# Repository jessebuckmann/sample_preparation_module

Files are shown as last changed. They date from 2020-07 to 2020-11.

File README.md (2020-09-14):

# Welcome!

You find yourself at the front page of the Utrecht Experiment Design course documentation, edition 2020. 

Welcome! :confetti_ball: :heart_eyes: :smile: :confetti_ball:

## From the course coordinator
 
I am thrilled to be your host in the second edition of the Utrecht Experiment Design (UED) course. My name is Sanli and my goal is to make this course the most memorable one in your program.

Part of the course syllabus is similar to other practical courses you have seen in the past. Other parts might seem a bit unusual at first (e.g. community interactions, story-telling, value exchange), but I hope that by the end of the course, they all make sense to you. Remember, the main goal of this course is to empower you (plural) to be a distinguishable cohort of experimental physics students. Making measurement setups that work and reporting on your experience are means to this goal.

Last year, UED was run for the first time. I had to make a good deal of planning only based on intuition. We had many engaging and constructive discussions and built part of the course structure together. Luckily, students, their mentors and the involved experts at the Physics department, told me they had an overall positive experience, and blessed me with well-intentioned constructive feedback. The course ended with a festive poster presentation. We even had cake and everyone seemed to be very pleased. Some of those students will be your mentors this year. 

## Schedule
From Thursday 3/9/2020 to Monday 2/11/2020
+ Mondays: 11h-18h, Minneart 002 and 004
+ Thursdys: 9:30-12h, MS Teams

+ Thursday, 5/11/2020: __Public Presentation__

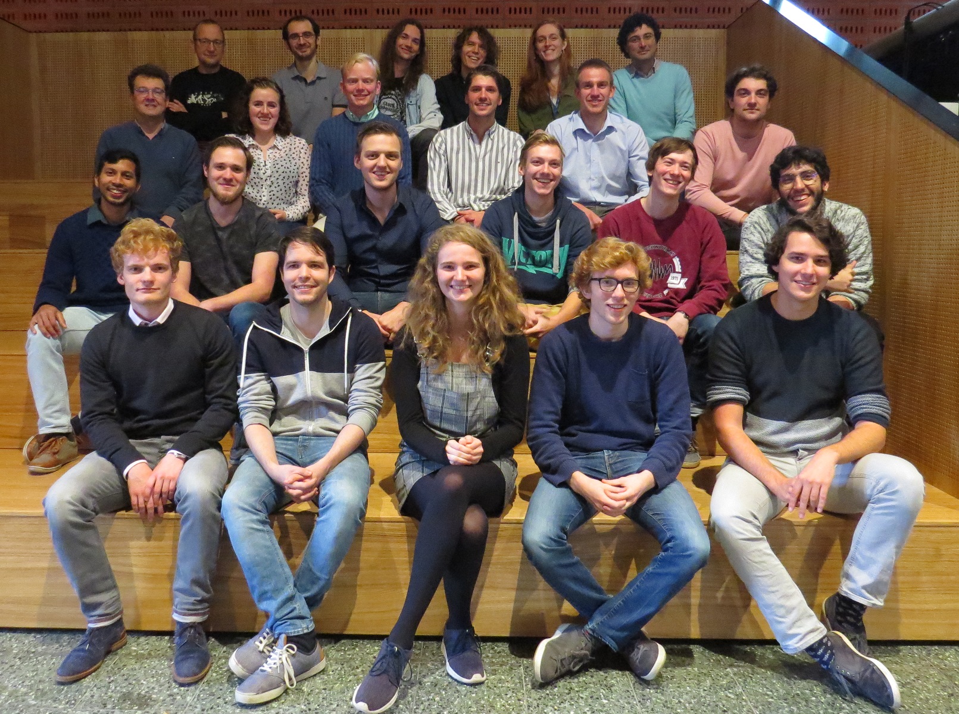
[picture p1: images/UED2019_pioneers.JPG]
cohort 2019

*Group photo with the "πoneers"*

This year, we are equipped with the experience and feedback of your predecessors and have planned a tighter framework. A major part of the course, still, will only be filled in based on your input. 

I hope that this guide can help you navigate through the logistics and instructions of this round. If anything is unclear or if you have questions that are not answered, please reach out to me directly. I am here to help.

#### how to reach me:
+ Email: s.faez@uu.nl 
+ Preferred mode of communciaiton: (direct) messaging on [MS-Team](https://teams.microsoft.com/l/team/19%3a4a388e116e894e4a9ec3a19e32c58294%40thread.tacv2/conversations?groupId=b36d7aae-63c5-44c9-a860-073e4ffd37ae&tenantId=d72758a0-a446-4e0f-a0aa-4bf95a4a10e7)
+ Office: Ornstein laboratory 266 (limited presence due to the Covid19 pandemic)
+ Twitter: [@sanli](https://twitter.com/sanli/)

The files in coordination directory contain most of the information about the course. To start, you can check the [syllabus of the course](Syllabus_2020.md) or check [how to contribute](CONTRIBUTING.md). The files in that directory will be updated during the course (fetch them into your local repo) and the imporant messages will be listed [in updates](UPDATES.md). To make our classes a welcoming and pleasant experience for all participants, please read the [code of concuct](CODE_OF_CONDUCT.md) very carefully, and stick to it.

#### suggestions are very welcome!
Please communicate all your suggestions to the course coordinator (Sanli Faez on MS-Teams) and do not make changes to this document without prior consultation.

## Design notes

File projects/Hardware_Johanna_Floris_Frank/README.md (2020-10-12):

**Welcome To The Hardware Project!** :raised_hands:

We, **Johanna**, **Frank** and **Floris** are the members of the Hardware-Group :v: .
The Hardware-Group aims to connect the techical parts of the box and to provide the experimentalists with a fast and save data transfer. 
Groups performing experiments and environment control give an Arduino-based text output.
The idea is now to connect these 'experiment Arduino's' as slaves to a central master Arduino, using which an I2C communication protocol may be established between them.
The master Arduino may then be read out by the computer running the data analysis and storage software.
The non-triviality lies in the fact that these slave Arduino's also serve as the master device within an experimental set-up by reading out the relevant sensor, which it must to upon request by the central master Arduino.
A more detailed report on context and theory, covering the I2C communication protocol and its main features (also compared to the frequently used SPI protocol), may be found [here](https://git.science.uu.nl/ued2020/experiment-design-2020/-/blob/master/projects/Hardware_Johanna_Floris_Frank/Documentation/Report_on_context_and_theory.md).

**The Experiment(s)**

The first step is getting an I2C communication protocol running between two Arduino's, where a slave sends a simple text message to the master upon the master's request using the [Wire library](https://www.arduino.cc/en/Reference/Wire).
This message may then be printed by the master.

Secondly, a very simple set-up was designed in which a single master Arduino reads out a BME/BMP280 environmental dummy sensor using the [Adafruit sensor library](https://github.com/adafruit/Adafruit_Sensor).

The aformentioned two slaves, i.e. a sensor and a slave sending a text message, were combined into a single-master dual-slave set-up, so that the master receives both measurement values and the text message.

To simulate an experiment Arduino connected to the central master Arduino, a single slave reading out the BME/BMP280 was connected to the master.
It was attempted to have a text tranfser - a data request from the master to the slave, in order to get the measurement startet. Then the slave should read out the data fromthe sensor to send the data as answer to the master.
This set-up did not end up working properly, presumably because the connection of the analog pins somehow leads to the sensor being recognized by the master.

**The Next Steps**

Considering the failure of the previously mentioned set-up, communication between the two Arduino's via the digital port was attempted.
A simple text-based I2C communication protocol between two Arduino's via the digital pins using the [SofwareSerial library](https://www.arduino.cc/en/Reference/SoftwareSerial) was achieved, altough as of yet they are poorly synchronized since the reading and printing my the master is much slower compared to the slave sending the message. (link)
If this is fixed, it should be possible to transfer sensor data between sensor and master upon request of the master. After that, a generalization to a connection with multiple (two for a start) masters may be made.

Should you want to reproduce these circuits, have a look at the [manual](https://git.science.uu.nl/ued2020/experiment-design-2020/-/blob/master/projects/Hardware_Johanna_Floris_Frank/Documentation/reproduction_guide.md).

Let's get this started :fire: !

**Cheerio !** :grin:

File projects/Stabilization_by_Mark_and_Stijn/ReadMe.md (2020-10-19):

In this ReadMe-file, we will place the manual for our folders, as well as our experiments. 

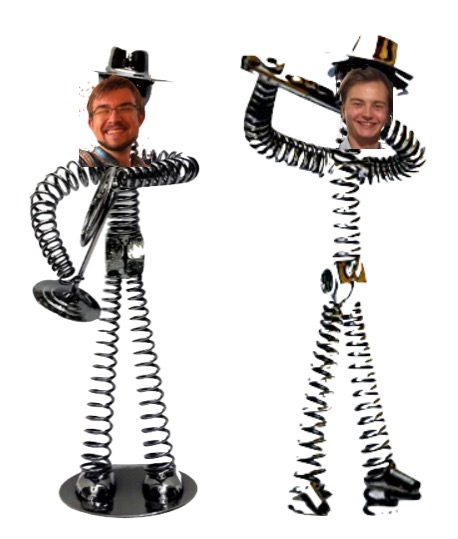
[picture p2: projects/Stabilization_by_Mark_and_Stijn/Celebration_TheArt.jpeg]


The purpose of our experiment was to be able to both see/filter out vibrations, as well as get/keep the experiment level (see our [canvas](project_canvas_-_Stijn_Mark.pptx)).

First off, before you start, we would advice you to get a cup of coffee. You got that? Good, time for the experiments then. 

**Leveling:**
We firstly thought that, in order to get the experiment level, we could use to yaw, pitch and roll (which is something the acceleromotor is able to measure). In the end, you'll find that there is a big problem with trying to do it this way, which is that it resets everytime you restart the acceleromotor. However, it's a good experiment to do, because you will find that this part of the acceleromotor is very precize. 

To do the yaw pitch roll measurments, only the arduino uno, MPU6050 and connectors are needed (in principle). With these components, the MPU6050 can be read out and that's all that’s needed (see ["List_Materials and Code_Used"](Measurements/List_Materials_and_Code_Used.md) for the arduino code that we used, along with our file that explains [how to use the arduino and MPU6050](Measurements/How_to_use_the_Arduino.md)). To do the calibration, a platform that can be rotated is needed. We used a machinist’s division table for this, but other platforms can be used. The machinist table is place in the upright position so (under the assumption that everything is straight) the z-axis of the chip is parallel to the gravitational vector. (again under the assumption we live on a flat earth with homogeneous gravity) When turning on the arduino it self calibrates to gravity so from that point everything is relative to that point. (this implies that for a reproducible result, the sensor needs to be booted in the exact same position)

When the sensor is setup and measuring the table can be rotated around the clock. This is done on increments of 1 degree from 0 < theta  < 10, than 5 degree intervals up to 90 degrees and from this point on only every 10 degrees to complete the circle. Whilst setting the angles it has to be taken in account that there is some mechanical give in the system. This could introduce a new error in the system when not dealt with correctly. To compensate for this give, the knob has to be put onder strain on the same side of each measurement point. This means either at the beginning or end of the give.  On each of the set angle points the yaw pitch and roll have to be manually read out. When all data is collected the points can be plotted in a program of your own choosing.

The Full Setup that we used can be found in the ["SetUp1"-folder](Measurements/Yaw_Pitch_and_Role_Measurements/SetUp).

The rest of the data and graphs that we gained, can be found in the ["YawPitchRole"-folder](Measurements/Yaw_Pitch_and_Role_Measurements).

**Vibrations:**
The main experiment that the "experiment-group" wanted to do, was the Cavendish-Experiment. This means that frequenties below 10 Hz will be "deadly" to the experiment. Our main objective thus became a little more specific than what we started with. However, we weren't able to find a good way to "create" these low frequenties (since low frequenties posses low energy), thus we also weren't able to measure them and thus see if our system could filter them out. Because of this, we have only taken a look at frequenties between 20 and 100 Hz, because those we could create and see. 

In a vibration experiment, one needs 3 things:
- Something that creates the vibrations
- A mass that vibrates, on which you can stick your measuring device
- A device on which you can see the data measured.

In our case, that something that creates vibrations became a bass-speaker. However, if one can't get a viable machine that gives off a constant frequency, you can also use one single strong wave(for example made by the hit of a hamer on the work-surface). Our bass-speaker had been secured to a woaden board, which we put on some form of dampening substance. The main reason that we started to use such a dampening substance, was because otherwise, the board would vibrate off the table. However, by doing this, we "accidentally" created a double-spring system, which is better at filtering out frequencies. 
On the other end of the board, we can then put our mass with our measuring device (the acceleromotor). Between the board and the mass, we can then prepare our system (this can be springs, a dampening substance, or in the easiest case: nothing). To see what has been measured, one has to take a look at what kind of acceleromotor one has. For our experiment, we used an acceleromotor that could directly be plugged into an oscilloscope, meaning that we could visualize the waves on there. In some cases, one can also plug the oscilloscope into the computer, and thus you can easily extract the data. In our case, we could only get possesion of a older type of oscilloscope, which wasn't able to do this (unless we would have found a floppy-disc and a way to get this floppy-disc into our computer).
However, one can also use the computer and the waveforms-programme of digilent, which is also able to visualize waves. The only thing that's left now, is to show how the system that you have taken a look at reacts to a certain frequency. This is done by making a bode plot, which can be done by a very good oscilloscope, but you can also do it by hand (which takes a lot longer).

If neither of these 2 is possible, one doesn't have to build our entire setup, in order to still be able to see that the accelerometer can measure waves. One can also "visualize" the waves by just directly looking at the acceleration-output that you get when running the arduino-file "MPU6050_DMP6" (see our arduino-explanation file how to find this). To do this, all you need is the arduino, the accelerometer and a work-surface. When looking at the raw data, you should see that the acceleration changes when you hit this work surface. 

The Full Setup that we used can be found in the ["SetUp2"-folder](Measurements/Acceleration_Measurements/SetUp). We als made a ["Materials and Code_Used"-file](Measurements/List_Materials_and_Code_Used.md) where you can find all the materials and code that we used for our setup.

The rest of the data and graphs that we gained, can be found in the ["RawSignals"-folder](Measurements/Acceleration_Measurements/RawSignals) and the ["FFT"-folder](Measurements/Acceleration_Measurements/FFT). As said before, we only have pictures of our data, since we weren't able to get an oscilloscope from which we could actually extract our full data. Because of this, there is also this added error-bar in our graphs. 

If you want to see more about what we did with our setup, see our [First Rapport](Rapport_after_first_weeks.md).

**Hazards:**
- If the people after us decide to also use a machinist’s division table (on the mill), keep in mind that you are working with heavy machinery. So first off, don't consume any alcohol while operating this machines, but also make sure the machine is turned off when you are changing the settings manually.
- Don't shake/drop the acceleromotor to much (nor the arduino), since this is fine equipment. 
- If you use a bass-shaker, keep in mind that it can vibrate off the worksurface, as well as overheat. 

**Needed Contact Information:**

Stijn Helsloot, s.helsloot@students.uu.nl

Mark Waterlaat, m.m.a.waterlaat@uu.nl

Dante Killian, d.killian@uu.nl (Contact person for equipment)

Rene Barthel, (Contact person for equipment)

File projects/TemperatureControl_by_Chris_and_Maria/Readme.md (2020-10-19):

Hello everyone!

We (Chris and Maria) are the team that deals with the temperature control of the box for the actual experiemnt!

Scope of the project:

We aim to measure the temperature and send the value each minute to the software team. Except from that, with the use of peltier we will cool or heat the box when is necessary. More about that you can find in the template_Article inside the file [documantation/data](https://git.science.uu.nl/ued2020/experiment-design-2020/-/tree/master/projects/TemperatureControl_by_Chris_and_Maria/documantation/data), where is also the schematic of the circuit and the code we use (so far).

About the instructions:

The instructions on how to reproduce the setup can be found in the file [Instructions](https://git.science.uu.nl/ued2020/experiment-design-2020/-/tree/master/projects/TemperatureControl_by_Chris_and_Maria/Instructions) together with some photos that will help you! We will soon add in that file the updated instructions based on our feedback. **Notice**: We are planning to make some more changes on our setup and we have not taken so far accurate measuraments so do not expect to take something. We will inform you through README about the changes we will have! The aim for now is just ro reproduce the setup. 

In the file [feedback](https://git.science.uu.nl/ued2020/experiment-design-2020/-/tree/master/projects/TemperatureControl_by_Chris_and_Maria/feedback) except from the peer feedback and by the Coordinators you will also find our response!

Here also you can find our canvas as well as our project and personal goals!

If you need further information on something and you believe that it should be here please contact us and we will fix it as soon as possible! :)

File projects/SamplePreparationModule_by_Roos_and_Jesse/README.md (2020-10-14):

### Sample preperation module
By Jesse and Roos

### Project description
In this project a Sample preparation module is build. It has some of the features typically found in a fumehood, but with an all new design. The sample preparation module enables the user to prepare samples without contaminations in a well ventilated area. The box will be modular, meaning that the user can perform multiple kinds of experiments within the box. The user can supply the tools that are needed for the specific experiment currently equiped in the off-grid lab. 

Typically a fumehood is a very expensive lab component. Looking at the [cost](https://git.science.uu.nl/ued2020/experiment-design-2020/-/blob/master/projects/SamplePreparationModule_by_Roos_and_Jesse/project_details/cost_breakdown.md), designing your own fumehood might have several advantages. Obviously you need to live up to some of the general features a fumehood must have e.g. ventilation and chemically resistant worksurface. Besides being much cheaper, you can design the fumehood in a way to simplify the sample preparation you need to do.

For the general construction of the fumehood the [building progress](https://git.science.uu.nl/ued2020/experiment-design-2020/-/blob/master/projects/SamplePreparationModule_by_Roos_and_Jesse/project_details/building_progress.md) is available, along with several [photos](https://git.science.uu.nl/ued2020/experiment-design-2020/-/tree/master/projects/SamplePreparationModule_by_Roos_and_Jesse/Photos) of the various stages of construction. While this construction might not live up to the features of a real fumehood, it does offer a degree of protection and a good working environment for the prepartion of some typical samples that are used in experiments.

For reproduction of builing the box you can read the [building progress](https://git.science.uu.nl/ued2020/experiment-design-2020/-/blob/master/projects/SamplePreparationModule_by_Roos_and_Jesse/project_details/building_progress.md). Testing of the box can be found in the [testing directory](https://git.science.uu.nl/ued2020/experiment-design-2020/-/tree/master/projects/SamplePreparationModule_by_Roos_and_Jesse/Testing). This directory contains two different testing procedures. One for the [airflow/ventilation](https://git.science.uu.nl/ued2020/experiment-design-2020/-/blob/master/projects/SamplePreparationModule_by_Roos_and_Jesse/Testing/testing_airflow.md) and one for the [chemical resistance](https://git.science.uu.nl/ued2020/experiment-design-2020/-/blob/master/projects/SamplePreparationModule_by_Roos_and_Jesse/Testing/testing_coating.md). For the reproduction of these testing results the instructions can be found in the [instructions](https://git.science.uu.nl/ued2020/experiment-design-2020/-/tree/master/projects/SamplePreparationModule_by_Roos_and_Jesse/peer_instructions) Here you will find an additional README to help you get started.

Main features:
- [ventilated](https://git.science.uu.nl/ued2020/experiment-design-2020/-/blob/master/projects/SamplePreparationModule_by_Roos_and_Jesse/Testing/testing_airflow.md), to carry away fumes
- [spill proof](https://git.science.uu.nl/ued2020/experiment-design-2020/-/blob/master/projects/SamplePreparationModule_by_Roos_and_Jesse/Testing/testing_coating.md), the workspace has high chemical resistance.
- [air tight](https://git.science.uu.nl/ued2020/experiment-design-2020/-/blob/master/projects/SamplePreparationModule_by_Roos_and_Jesse/Testing/testing_airflow.md), ensure that the fumes will only go out through the pipe.

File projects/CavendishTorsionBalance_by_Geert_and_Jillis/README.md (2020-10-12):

# Cavendish Torsion Balance

Welcome to the folder which contains all the information on the Cavendish Torsion Balance project.  

The project is run by Jillis Schokking (j.b.e.schokking@students.uu.nl) and Geert Schulpen (g.h.a.schulpen@students.uu.nl).
You can reach us by [MS teams](https://teams.microsoft.com/l/channel/19%3a17671f7d35194c9aa6a368c449fd96fe%40thread.tacv2/grand%2520project?groupId=b36d7aae-63c5-44c9-a860-073e4ffd37ae&tenantId=d72758a0-a446-4e0f-a0aa-4bf95a4a10e7) or in person if we by chance are around. 

## Description of the project
We try to measure the gravitational constant G by way of a torsion balance, which was first done by [Henry Cavendish](https://www.jstor.org/stable/106988). The current setup is a redesign of the basic setup as used by first year students. This was necessary due to the size constraints of the modular experiment box. The experiment setup is almost finished, and can be used in its current state to measure the gravitational constant. A short overview of the context and theory for the experiment can be found [here](ContextAndTheory.md). An instruction manual for working with the setup can be found [here](instructionManual.md). Proper measurements will require carefull calibration. 

## Current state of the project (roadmap)
At present, our setup should be able to measure the gravitational constant. Electronic elements are plug and play. Only the installation of WaveForms is required. In its current state we have completed the following items:
- Found a temporary bed with enough vibrational damping.
- Moddeled and 3d printed all necessary structural parts
- Implemented a way to measure angles (Digital Discovery 2, Laser, Sensor and Modulator)
- Automatic rotation of the outer ring (Arduino, belts, servo's)
- Construction of the halter.

The following items still need to be finalized:
- Construction of a proper bed that fits in the modular experiment box.
- An automatic release mechanism for the torsion balance.

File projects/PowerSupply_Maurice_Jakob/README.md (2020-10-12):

# List of files you may be looking for (if not, ignore this section)
- [Report context and theory](./documentation/report_context_theory.md)
- [Project goals](./documentation/project_foals.md)
- [Instructions](./documentation/Instructions.md)
- [Personal goals Maurice](./documentation/Personal_Goals_Maurice.md)
- [Personal goals Jakob](./documentation/personal_goals_jakob.md)

# Power supply for Experiment box

In this subproject considerations and the design of a power supply that suffices for the needs required are made.
The goals of this project are briefly presented in the [canvas](./documentation/project_canvas_ps.pptx) and further elaborated in this [report](./documentation/report_context_theory.md).

To settle on the right approach a comparison between different levels of DIY was made which can be found [here](./documentation/Comparison_powerbank_DIY.md).
The major difference is the level of knowledge regarding electronics required to build it.

A current list of parts for this project can be found [here](./documentation/list_of_components.md).
The current plan consist of a powerbank (5V), 12V lead acid and inverter to provide all the needs specified.
A load-switch and monitoring system will provide the safety and communication with other parts of the box.
It is further expanded with a solar panel to charge the station remotely.

How to put everything together is documented in the [instructions](./documentation/Instructions.md). 
There is also a separate [documentation](./documentation/Arduino/Arduino_Instructions.md) about monitoring the battery voltage with the use of an arduino.

### Our first milestone
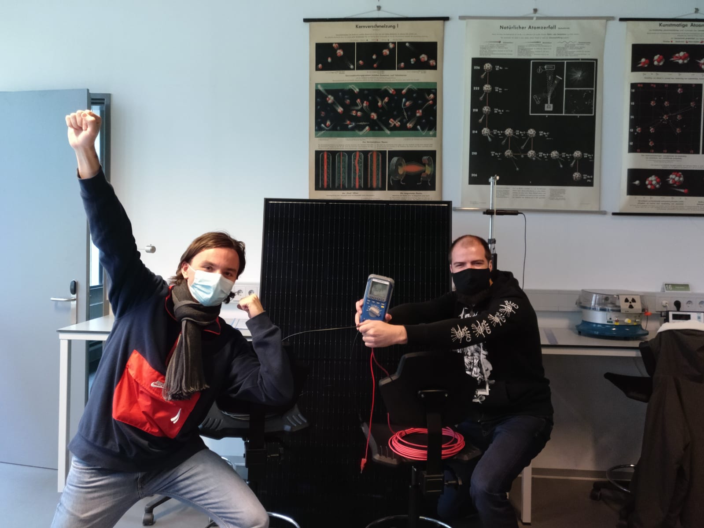
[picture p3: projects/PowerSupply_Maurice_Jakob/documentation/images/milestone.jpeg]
milestone


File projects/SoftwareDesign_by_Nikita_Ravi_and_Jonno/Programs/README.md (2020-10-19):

Hi honorable User!

If you haven't already, please first follow the [installation guide](projects/SoftwareDesign_by_Nikita_Ravi_and_Jonno/Installation_guide.md). 

There are four options to use the program.
1. Measure using a real Arduino and Analog Discovery 2
2. Measure using a real Arduino and a simulated Analog Discovery 2
3. Only use a real Analog Discovery 2
4. Only use a simulated Analog Discovery 2

See below on how to set up each one of the four options.

Once you get the BIMBO up and running, you can navigate through the tabs and press the start/stop buttons to start measuring. When pressing scan on the Analog Discovery 2 tab, a window pops out which allows you to scan the data and save it over time. If you browse to save the file, it will save as a .nc. However, you can still change the extension before you save it to for example csv. You can also edit the file path by just typing in the textbar instead opening the browse window. Whatever extension is there, if you open it with notepad it will still be in the csv format. The is an example output file [here](projects/SoftwareDesign_by_Nikita_Ravi_and_Jonno/Programs/Example_Measurements/exampleMeasurementAD2.csv). If you have ticked the Store config box it will also save a file with your config that looks like [this](projects/SoftwareDesign_by_Nikita_Ravi_and_Jonno/Programs/Example_Measurements/exampleMeasurementAD2.yml).  

For scanning any data coming in via an arduino, e.g. temperature or pressure, press 'start scan' in the designated tab. This will start an invisible scan in the background. Pressing 'stop scan' will terminate the scanning procedure and create a .txt file in the source folder with the acquired data in the format: 

\[TemperatureArray]   
\[TimeArray]

For examples see [here](projects/SoftwareDesign_by_Nikita_Ravi_and_Jonno/Programs/Example_Measurements/exampleMeasurementTemp.txt) and [here](projects/SoftwareDesign_by_Nikita_Ravi_and_Jonno/Programs/Example_Measurements/exampleMeasurementPres.txt).

If you would like to use an Arduino. Please make sure it outputs the data in the format: time(in ms),temperature(as float),pressure(as float). If you have no way of getting actual data from an arduino, or don't know how, you can simply make it output simulated data in the correct format by uploading [simulation_for_arduino.ino](projects/SoftwareDesign_by_Nikita_Ravi_and_Jonno/Programs/simulation_for_arduino.ino) to your arduino by using the [arduino IDE](https://www.arduino.cc/download_handler.php?f=/arduino-1.8.13-windows.exe)! In case you are using an Arduino Due, be sure to use the programming port on the arduino to upload any programs, it's the micro-usb port closest to the power input.

A list of known bugs can be found [here](/projects/SoftwareDesign_by_Nikita_Ravi_and_Jonno/Programs/Bugs.md).

In preparation of any of the four following options, open your preferred Python IDE and open the five .py files in experiment-design-2020-master\projects\SoftwareDesign_by_Nikita_Ravi_and_Jonno\Programs

**1. Arduino + real Analog Discovery 2**
- [ ] In the BIMBO_Interface.py uncomment the ArduinoWidget import in line 1.
- [ ] Uncomment the import from line 16 where the real controller is imported.
- [ ] Comment the import from line 17 where the simulated controller is imported.
- [ ] Uncomment lines 71 and 72 where the tabs for the Arduino are added .
- [ ] In order to start using the program, it is essential you plug in the Arduino measurement unit and make sure that it is outputting data in the required format.
- [ ] Once you have done this you have to check which COM-port is used to communicate with the device. This can be done in Windows by opening *Device Manager* and finding **Ports**. There it will say what COM-port is used. For Mac type ls /dev/* in the terminal to find the com port in the form /dev/tty.usbmodem* where * is the number. 
- [ ] FOR WINDOWS: Now go to the ArduinoWidget.py file and change the 'COMX' in line 17 to whatever COM is used by your device.
- [ ] FOR Mac: Change line 17 to: arduinoData = serial.Serial(port='/dev/tty.usbmodem14201', baudrate=9600)
.
arduinoData = serial.Serial(port='/dev/tty.usbmodem14201', baudrate=9600)

You are all set to go, just run the BIMBO_Interface.py with a Python interpreter in for example Spyder!

**2. Arduino + simulated Analog Discovery 2**
- [ ] In the BIMBO_Interface.py add the ArduinoWidget import to line 1 if it is not there.
- [ ] Comment the import from line 16 where the real controller is imported.
- [ ] Uncomment the import from line 17 where the simulated controller is imported.
- [ ] Uncomment lines 71 and 72 where the tabs for the Arduino are added.
- [ ] In order to start using the program, it is essential you plug in the Arduino measurement unit.
- [ ] Once you have done this you have to check which COM-port is used to communicate with the device. This can be done in Windows by opening *Device Manager* and finding **Ports**. There it will say what COM-port is used. For Mac type ls /dev/* in the terminal to find the com port in the form /dev/tty.usbmodem* where * is the number. 
- [ ] FOR WINDOWS: Now go to the ArduinoWidget.py file and change the 'COMX' in line 17 to whatever COM is used by your device.
- [ ] FOR Mac: Change line 17 to: arduinoData = serial.Serial(port='/dev/tty.usbmodem14201', baudrate=9600)

You are all set to go, just run the BIMBO_Interface.py with a Python interpreter in for example Spyder!

**3. Only real Analog Discovery 2**
- [ ] In the BIMBO_Interface.py remove the ArduinoWidget import from line 1.
- [ ] Uncomment the import from line 16 where the real controller is imported.
- [ ] Comment the import from line 17 where the simulated controller is imported.
- [ ] Comment lines 71 and 72 where the tabs for the Arduino are added.

You are all set to go, just run the BIMBO_Interface.py with a Python interpreter in for example Spyder!

**4. Only simulated Analog Discovery 2**
- [ ] In the BIMBO_Interface.py remove the ArduinoWidget import from line 1.
- [ ] Comment the import from line 16 where the real controller is imported.
- [ ] Uncomment the import from line 17 where the simulated controller is imported.
- [ ] Comment lines 71 and 72 where the tabs for the Arduino are added.

You are all set to go, just run the BIMBO_Interface.py with a Python interpreter in for example Spyder!

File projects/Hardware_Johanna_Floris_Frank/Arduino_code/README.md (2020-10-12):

**digital_master and digital_slave**

Simple scripts for I2C communication between a master and slave Arduino via the digital pins.

**master_reader and slave_reader**

Simple scripts for I2C communication between a master and slave Arduino via the analog pins.

**BME**

BME.ino can be uploaded to a master Arduino connected to a single (BME) sensor and possibly a slave Arduino. The master Arduino then reads the sensor output and, if present, the text-based message the slave sends directly. Should you want to use the second Arduino, the slave_reader.ino sketch should be uploaded to the slave device.

**Hybrid_Master and Hybrid_Slave**

The hybrid experiment has a network of multiple Arduinos being able to send data to a master Arduino. Hybrid_Master.ino can be uploaded to an Arduino, which then acts as the master Arduino requesting data from subscriber (slave) Arduinos and shows this data. Hybrid_Slave.ino can be uploaded to Arduinos connected to (BME) sensors. These subscribers then read the sensors and give the data to the master upon request.

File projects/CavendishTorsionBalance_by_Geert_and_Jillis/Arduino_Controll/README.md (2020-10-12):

The other file in this directory has the code to control the arduino and continuous servo for the Cavendish Balance.  
To control the arduino open this in the [arduino web editor](https://create.arduino.cc/editor) (or in your own local installation of the arduino editor). 
Set the board/port dropdown to "Arduino Due" and open the Serial Monitor from the sidebar.
You can send the code to the arduino by clicking on the arrow next to the board/port dropdown, the arduino will send a "hello world" message when the initiallization has worked.
More information on the arduino web editor can be found [here](https://create.arduino.cc/projecthub/Arduino_Genuino/getting-started-with-arduino-web-editor-on-various-platforms-4b3e4a)

The controller assumes the balls are in a neutral position at the start, they are midway between both measurement positions.
The turningtable is controlled by sending single characters to the arduino; E, L, R, S, l and r.
- S will turn the turningtable from the neutral position to one of the measurement positions
- E will turn the turningtable from one of the measurement positions to the neutral position
- L or R will turn the turningtable from one to the other measurement position
- l or r will turn the turningtable slightly in the same direction as L and R respectively

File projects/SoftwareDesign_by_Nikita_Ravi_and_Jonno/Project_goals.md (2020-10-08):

*Utrecht Experiment Design 2020*

# Project goals

### POP

+ **Purpose**: to define your targets for the project you have chosen and to keep your eyes on the ball 
+ **Outcome(s)**: list of checks and measure for evaluation of your project
+ **Process**: self-reflection and discussion with your mentors

PROJECT NAME: Software Design
PROJECT MEMBERS: Mikita, Jonna, Ravi

## Project goals (fill this at the start of the course)
* We want to make an intuitive program that can be used by people without any experience
* We want to be able to visualise data in said program
* we want to be able to adjust sensors in said program if needed
### Subgoals
* Make the model part
* Make the controller part
* Make the view part
* Transfer the sensor-signal to data
* Make an artificial data stream to test the model and interface

## Mid-course review of goals (fill this mid-course)

* We want to make an intuitive program that can be used by people without any experience
* We want to be able to visualise data in said program
* We want to be able to adjust sensors in said program if needed

Subgoals

* Create an arduino controller
* Adjust the AD2 controller (save files into text, voltage vs time)
* Make the general interface with tabs
* Make an artificial data stream to test the model and interface (CHECK!)

## Final review of goals (fill at the end of the course)

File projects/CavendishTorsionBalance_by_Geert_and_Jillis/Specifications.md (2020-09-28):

# Power

| | |
| ------ | ------ |
| Operating Voltage | 230 V (modulator), 5V (servo's) |
| Power Usage | We have to check (probably fairly low; small laser (1mW output) and a light sensor) |
| input type | AC |

The input voltage goes into a modulator to make the setup filter outside light. It directly controls the LASER and sensor. These use a much lower voltage. As such the modulator includes a transformer to transform back down to ±5V and ±8V. We feel it should be possible to cut out this transformer and directly feed the modulator, but the lab technician says otherwise for now. The 8V channel would need to be balanced.

# Size
| direction | size (cm) |
| ------ | ------ |
| width | 30 |
| depth | 50 |
| heigth | 35 |

# Vibration control
The experiment is vulnerable to low frequency vibrations. The natural frequency of the balance is 1 Hz. Therefore a low pass frequency dampening system with a threshold of 0.1 Hz would be desirable. 0.1-10 Hz couples strongly to our pendulum.

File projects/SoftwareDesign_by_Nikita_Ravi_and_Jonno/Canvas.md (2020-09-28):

# Problem
1. The raw data from the sensors is not processe
2. The processed data is not displayed
3. There is no way to control the sensors

# Solution
Make an intuitive UI that shows the current sensor values and can send data to sensor. 
It should also be able to save the data for analysis.

# Key metrics
* The data is correctly displayed and devices can be controlled. 
* This can be tested with artificial data stream.
* You should be able to use the interface with very minimal training. 
No programming knowledge needed, only a small one page explanation about the program.

# Resources required
* A display and raspberry pi (could also be combined as an external laptop)
* Data from the sensors
* Python knowledge about GUIs and controller
* Know which protocols are used
* Packages for those protocols and labphew package
* Power supply for raspberry pi or to (slowly charge laptop)

# Contributor Profiles
The contributors will be people on the internet that made open source packages.
Ideally, a contributor has extensive programming knowledge and has worked with interfacing before.
The other contributors will be the people that provided the data and hardware.

# User Profiles
Our early adopters will be the people that build the sensors. 
They will rely on our interface to do measurements.
The final users will be the people that make use of the measurement station.
They will need it to controll the device and make actual use of it.

# Contributor Channels
Once people want to introduce new sensors, our program should be good enough to build upon.
This way they will not have write their whole thing from scratch but can use/edit/incorporate our program.

# User Channels
They have basically no other options apart from writing a program themselves.
What we should do is make a program that is good enough that they will not want to write their own.

# Unique Value Proposition
We will make sure that even people that do not have programming experience or knowledge can still use our device.
Our project will also greatly simplify the use of the box.
It is also needed to connect the different parts of the box to be able to do a cohesive measurement.

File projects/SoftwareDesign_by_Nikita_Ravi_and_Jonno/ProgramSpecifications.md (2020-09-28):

| **Component**                | **Specs**                                                    | **Done by** |
| ---------------------------- | ------------------------------------------------------------ | ------ |
| General interface            | * Dropdown button/tabs to swap between controllers<br />* Exit button<br />* Window to display graphs<br />* Overview mode of all graphs<br />* Ability to save data |Ravi        |
| Digilent AD2 Controller      | * Live feed of the inputs (from AD2 to computer) <br />* Ability to control outputs (from computer to AD2)<br />* Ability to save the inputs over time |Mikita       |
| Arduino text base controller | * Ability to display live feed of text-based inputs (from Arduino to computer)<br />*Ability to save inputs over time |Jonno        |

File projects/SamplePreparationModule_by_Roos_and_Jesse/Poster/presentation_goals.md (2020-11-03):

# Experiment Design 2020

## Symposium self-reflection

project, team: Sample preparation module, Roos de Boer and Jesse Buckmann

The purpose of this self-reflection is to learn from the exercise of presenting your project to a public audience. Answer the preparation questions **before** the online symposium and evaluate them based on your experience **after** the end of the symposium

## Preparation

### Content: 
+	What makes your pitch attractive? 

- Suggestions of possible problems/negatives and explaining how they are not present.

+	What do you want the visitors to learn from your pitch? 

- What the purpose of the sample preparation module is. 

+	What elements have you deliberately put in your presentation to reach your goal?

- Comparison of the sample preparation module to an actual fume hood so you can see the advantages of the sample preparation module.
- Mentioning problems and stating that the sample preparation module is the solution.

### Performance:
+	What is **your** goal of presenting your pitch?

- For people to become interested in the sample preparation module and for them to think of it as a good alternative for the fumehoods.

+	What do you want the visitors to remember after coming to your discussion room?

- That the sample preparation module is cheap, easy to build and widely applicable.
- That you can still do experiments in times of Corona.

+	Which indicators show to you that your visitors are engaged with your message?

- They understand the advantages of the sample preparation module and might consider how it could be applicable in certain situations.

## Evaluation
+ 1.	What worked well about your pitch and presentation?
+ 2.	What did not work as you expected?
+ 3.	Considering your own indicators, how do you evaluate the success of your final presentation?
+ 4.	What feedback have you received from the visitors about the project and about your way of presenting it?

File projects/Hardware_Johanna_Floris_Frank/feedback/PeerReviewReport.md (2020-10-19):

# Reproducibility report

## Experiment/team: 
Hardware by Floris, Frank and Johanna

## Reviewers: 
Geert, Maria and Olaf

## Report 

### Documentation:

1.	Could you understand the purpose of the experiment? Explain.
The purpose of the experiment is to rebuild three set-ups connecting different arduinos and sensors. Within the larger project this is of importance since we want all the different components to be connected to each-other and to have communication between them. 

2.	Were the safety instructions clear?
Yes, since there were no safety instructions they were clear.

3.	How helpful is the documentation for reproducing the measurement?
The documentation was not quite complete. It is assumed that you have prior knowledge of arduino's and of the hardware. It would have been helpfull if the instructions would have included more detail on the placement of the wires (e.g. to which pins in the arduino the sensor had to be connected) in the arduino and or the sensors. It would have helpful as well if there would have been more instructions on what every element does and how it looks like (e.g. we did not know what the sensors look like and could not find them in the beginning).

4.	Did you get stuck at some point? What extra help did you need to proceed?
Yes, from the instructions alone it was not clear if we needed to use one arduino, or use them both at the same time. Luckily this was mentioned briefly in the readme so with that information we were able to figure out the set-up. Also, Maria and Geert had prior knowledge of working with arduinos and breadboard so we did not have to look up how they work in more detail to reproduce the set-ups

5.	Are you guided to reproduce previous measurements? How easily could you navigate through the project documentation?
The links to the necesarry sketches were placed in the instructions so this was quite convenient. We did miss clear goals by which we could check if our set-ups lead to the same results as the project group. We had no way of checking this. It was possible to deduce this for the first two set-ups from the code but not for the third set-up.

6.	What can be improved in the documentation?
The instructions could be improved by adding schematic drawings of each set-up. This would make the placing of all the components and wires clearer and easier to reproduce. Also provide a clear goal to the experiment, what should each set-up do exactly? How can we confirm if it is working properly?

### Measurements:

1.	Can you operate the setup with the provided instructions?
We answered this question in the previous part.

2.	How close were the results you obtain to the previously reported results?
We do not know precisely since we do not know the exact results the project group obtained. We did find however that the arduino's and sensors were communicating with the master arduino.

3.	Can you understand and explain the analysis procedure to a third person?
Not really since there is no analysis procedure. I think I have a general sense of how the code works but I could not explain it in detail.

4.	Is the setup robust and safe to operate? 
Yes it was safe

5.	Did you encounter any issues? Could you troubleshoot those without contacting the owners?
Yes, we did not know how the sensor looks like. We were able to troubleshoot this by googling for the name of the part we did not recognize.
We also had problems with how to connect the sensor to the arduino, but that was solved by trying a couple of variations.

6.	What part of the measurement procedure did you appreciate most?
It is nice that the Arduinos can communicate.

### Interactions:

1.	Could you relate to the stated goal of the project?
Yes, we also want to be able to control the different elements in the box from one central place.

2.	Which instructions did you need from the owners on top of the written files?
We could had asked them the results they had in order to know if ours were correct.

3.	Does the experiment accomplish its stated purpose?
It is not accomplished because the data from the sensor could not reach the second arduino. However, the owners of the project are already aware of this.

4.	What do you recommend to the project owners to improve their complete package?  
It seems that the problem in the Hybrid codes comes from the fact that a float-type has to be cast to a byte-type and this is not done explicitly.
It might be that [this](https://forum.arduino.cc/index.php?topic=577373.0) web-page can help with this.
The master arduino does send output when wiring incorrectly (SCL-A4 slave-A4 master, SDA-A5 slave-A5 master), maybe this helps in solving the problem, it did not send output when wiring correctly, as indicated by one of the owners of the project.
It would be nice to create a wiring diagram/pictures of the final setup.
It would be nice to include some documentation for people who did not yet work with an Arduino yet.

## Respone from project group: 
Thank you for the documentation.
It was indeed a bit vague how to connect the wires based purely on text. Wiring diagrams for the different set-ups are now included, as an overview diagram of an Arduino UNO board and the sensor. 
Hopefully this also solves probles regarding the recognision of the sensor component.
 
In our experience, the desired output was somewhat clear from the description of the set-up itself. 
However, since your experiences were different, a have added this more explicitly to the reproduction guide.
In addition, a mre detailed description on what the COM port output should read if the set-up is repeated.

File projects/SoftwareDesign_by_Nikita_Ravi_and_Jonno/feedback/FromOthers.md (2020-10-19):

## notes

complicated with the installation files, could be prepackaged in a zip  
**This could indeed be done, be would need to be redone everytime a file changes. So for now we will leave it like this.**  

labphew installation caused many issues, but we managed to get it working on one machine.  
**Nice you at least got it working on one machine.**  

Then a second readme about the usage start with "once you get the BIMBO up and running", it feels like some intermediate steps are missing that connect the two files.  
**Added meaning of BIMBO to the first README.**  

Could use some additional steps for the installation of the arduino or make it clear if its necesary or not, given the pre-installed arduino  
**We do not really know how to make it cleared, as there is already an explanation of how to upload a simulation program to an Arduino. We could have more clearer stated that the Arduino's given to you were already preinstalled. Also, the issue of data output is more something for the sensor people.**  

Steps for finding COM port are seperated, even though they are a single step. was slightly confusing.  
**Yes good point. Edited this in the README to make it one step.**  

unclear where the savefile goes for AD2, it says a path, which does not exist on the user's PC. Browse button does not work, gives error in spyder 'model labphew has no attribute 'parent_path''.  
when trying to save to a new path by writing it, it gets permission denied or no such file or directory.
**We were not able to reproduce this bug. For us the browse button works. There is also a default path already written, which you can edit to you own path by typing. You can also change the default path in the config file if you want (though this was not stated anywhere)**  

BIMBO can only be run once per spyder instance, only restarting spyder enables to run the script again.
replugging arduino does the job as well, or use a different IDE. Doesn't happen on MAC  
**This seems to be a spyder issue. Also does not happen on every machine. We do not really know how to fix this. We could in the future change the installation guide to use pycharm but we are not sure this will not happen there either.**  

the fixes for arduino read-out are using: 

In command prompt: 

ls /dev/*

To find the com port in the form /dev/tty.usbmodem* where * is the number. 

Change in the ArduinoWidget line 17: 

arduinoData = serial.Serial(port='/dev/tty.usbmodem14201', baudrate=9600)  #Rename the 'COMX' here to whatever COM is used by your device.  

**Added this to the README, thanks!**

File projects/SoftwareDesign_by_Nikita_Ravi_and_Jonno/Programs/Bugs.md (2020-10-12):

**Below a list of known bugs.**

* Sometimes the program draws weird lines when the measurement is start in the case of the Arduino widget.
* When starting multiple measurements with the Arduino/AD2 the program seems to slow down a lot.
* Very long measurements could possibly run into memory issues.

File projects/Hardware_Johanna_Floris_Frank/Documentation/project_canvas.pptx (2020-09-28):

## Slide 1

Hardware

Collecting/structure the ideas of the Cohort
Provide the hardware for data transfer/display
Install the hardware

Outline the parts of experiment(s)
->Collecting whats needed,
wire the sub and central facillities

The data transfer has to work, with an adeque number of inputs (decided by input of other groups). Transfer speed/bandwidth should be tested. Signal-to-noise ratio should be minimilized.

-Information on other subprojects,
-Electrical wires, means of shielding or differential signalling, microcontroller (raspberry pie).
-Input from mentor (Kira) and (possibly) Dante (expert)

-For the box to function as intended in its entirety, data transfer between measurement stations/sensors needs to be transferred to a central place for display/extraction
-Input and output ideas of other groups need to be considered and made compatible

-Software group
-Experimentalists (both other groups and general users of the off-grid measurement station)

-Discuss with software group for hardware requirements

-Discuss with relevant groups with
-A general list of questions for data input groups

-Power supply, box design, environment control groups
-Groups designing experiment modules

See next slide for instructions!

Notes: Go to File > Make a Copy… to make your own canvas
See next slide for instructions

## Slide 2

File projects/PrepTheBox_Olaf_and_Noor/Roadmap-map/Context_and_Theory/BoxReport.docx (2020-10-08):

Prep the Box project

Concept and context

The goal of Experiment Design 2020 is to create a modular, off-grid measurement system to perform experiments (almost) anywhere in the world without the need of external hard- and software. A project like this consists of many different sub-projects concerning the power supply of the box and the environmental control systems. However, all these sub-projects must be placed somewhere, shielded from the environment in some way. The Prep the Box project is the sub-project that takes care of the casing and interior structure of the off-grid measurement system. An important, hands-on project essential to the mail goal, since without a proper framework there will be no off-grid measurement system.

This project started with a box on wheels made from metal beams with a wooden floor and plated sides and a roof, all of which can easily be assembled and disassembled. Our job was to create a suitable casing from this box, in which all other groups can place their components, creating the off-grid measurement lab. An important note is that as a group we required that the measurement system should be modular, i.e. all the hardware components should be easily replaceable to redesign the box for different experiments.

We started by having discussions with all the different groups to see which specifications the box should meet and to get an idea for the general design of the box. A consensus was reached that the top part of the box would hold all the hardware needed to run the experiment (power supply, temperature control, vibration measurements etc.) and the bottom part would hold the experiment unit, encased by a vibration isolation chamber. Furthermore, the box should be watertight, since it is must be able to withstand rain, and it should be able to maintain a temperature inside the box in which the hardware can function.

The modularity of the top part of the box (containing the hardware) will be made up from rails, suspended from the ceiling. Different hardware modules can be placed in these rails and then connected. By placing the modules in rails suspended from the ceiling it will be easier to create an air flow between the different elements to either cool or slightly heat-up the modules. The vibration isolation chamber will be fastened onto the framework of the bottom part of the box. Inside this chamber one can then place its experiment modules.

The main part of this project was to communicate with all the different sub-groups. Each sub-project requiresd a certain amount of space and in the box only a limited amount of space was present. As in all projects, it was a process of negotiation, making concessions and taking the limitations into account for the final design of the box.

As for the final design, some tests will be carried out in order to see whether our chosen adjustments have been the correct ones. One test one could think of is for example the adjustable leg system to make the box even on terrains with differing slopes, and measuring the temperature in the watertightly sealed box when a warm object is placed inside to see whether we need to add ventilator shafts.

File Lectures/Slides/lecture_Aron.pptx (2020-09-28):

## interfacing electronic devices using Python and labphew

Aron Opheij
Experiment Design 2020 course
10-09-2020 Utrecht University
Version 0.2

## This lecture

- Some philosophy of lab automation and structuring code
- Introducing the labphew package (watching me)
- Helping you fork and install the labphew package (together)
- You exploring it yourself (if there is time)
Two important comments:
- All of this is a work in progress
- It’s ok if you don’t understand everything today. This lecture serves as an introduction, after which you can explore at your own pace and ask us for help

## Automating experimental setups

- When doing experiments you may quite quickly find yourself wanting or needing to automate your experimental setup. Some possible reasons may include:
  - You want to speed things up
  - Certain actions have to be performed quicker than possible by a human
  - You have to repeat something many times
  - You want to prevent human mistakes (due to boring repetition)
- To achieve this you’ll have to write code to control devices.

## A pitfall during development

- You start with writing code to solve a small automation task (e.g. perform a single simple experiment with a single device).
- Then it turns out you want to add complexity to the measurement procedure or the experimental setup (add more devices perhaps), and you add this to your code.
- As this continues it becomes harder and harder to modify and maintain your code. It becomes harder for yourself to understand and impossible for someone else.

## The onion principal: layers

- In order to write expandable code it is important to split your code up in (smaller) encapsulated chunks.
- The classes of Object Oriented Programming (OOP) are perfectly suited for this purpose.
- These chunks can act as layers of an onion, one building on top of the other.
- These can then more easily be modified or exchanged without having to worry about other parts of the whole code.
- It is not always obvious where and how to split code up. Try to think about: how much would the rest of my code have to change if I make changes to this section?

## intermezzo on classes

- Python classes allow you to create an object that has internal memory (variables/attributes) and functionality (functions/methods)
- These internal variables and functions can be accessed and executed. (Much like a measurement device)
- Nomenclature (for when you get confused)
  - What you define is called a class. It is basically a “type” (just like integer or string, but one that can be very complex)
  - Only once you have typed a = 5, a is a variable of type integer
  - In the same way you first need to “create an object of that class” or “instantiate the class”. b = MyClass(). Now b is an instance of MyClass or an object of class MyClass
  - The ‘functions’ inside a class are called methods
  - The ‘variables’ inside a class are often referred to as attributes (but be careful attribute is technically a broader term that also includes methods)

## Controller – Model – View in context of labphew

- Controller
  - Is specific to a device
  - Contains code to communicate with the device and possibly other code to make interacting with the device easier
  - Note for developers:
    - There exist “message-based devices” for which all communication happens as text commands over serial communication and devices which have their own driver/dll (these often prove a bit more difficult) and devices without a computer interface but that you operate by changing a voltage for example (you then need a device for that)
    - Often you can find that someone in the online community has already written something for a device. Otherwise you’re going to need the manual
- Model
  - Is specific to an experimental setup
  - We call the classes inside a model Operator
  - When creating the Operator object one would pass one (or more) controllers as input arguments. These are the devices used by the Operator to perform a scan/experiment
  - The Operator should contain several “functions“ (methods):
    - To connect to the devices (with the controllers it was given as input)
    - Also to disconnect
    - To run a scan (experiment) (there could be multiple of such functions for different scans)
    - To save data
    - For live plotting in a graphical user interface (if you need that)
- View
  - Allows you to interact with the Operator in a graphical user interface (GUI)
  - This has two classes which we call: MonitorWindow (for continuous a live “plotting”) ScanWindow (for performing a scan)

## Controller – Model – View in context of labphew

- Controller
  - Is specific to a device
  - Contains code to communicate with the device and possibly other code to make interacting with the device easier
  - Note for developers:
    - There exist “message-based devices” for which all communication happens as text commands over serial communication and devices which have their own driver/dll (these often prove a bit more difficult) and devices without a computer interface but that you operate by changing a voltage for example (you then need a device for that)
    - Often you can find that someone in the online community has already written something for a device. Otherwise you’re going to need the manual
- Model
  - Is specific to an experimental setup
  - We call the classes inside a model Operator
  - When creating the Operator object one would pass one (or more) controllers as input arguments. These are the devices used by the Operator to perform a scan/experiment
  - The Operator should contain several “functions“ (methods):
    - To connect to the devices (with the controllers it was given as input)
    - Also to disconnect
    - To run a scan (experiment) (there could be multiple of such functions for different scans)
    - To save data
    - For live plotting in a graphical user interface (if you need that)
- View
  - Allows you to interact with the Operator in a graphical user interface (GUI)
  - This has two classes which we call: MonitorWindow (for continuous a live “plotting”) ScanWindow (for performing a scan)

## Controller – Model – View in context of labphew

- Controller
  - Is specific to a device
  - Contains code to communicate with the device and possibly other code to make interacting with the device easier
  - Note for developers:
    - There exist “message-based devices” for which all communication happens as text commands over serial communication and devices which have their own driver/dll (these often prove a bit more difficult) and devices without a computer interface but that you operate by changing a voltage for example (you then need a device for that)
    - Often you can find that someone in the online community has already written something for a device. Otherwise you’re going to need the manual
- Model
  - Is specific to an experimental setup
  - We call the classes inside a model Operator
  - When creating the Operator object one would pass one (or more) controllers as input arguments. These are the devices used by the Operator to perform a scan/experiment
  - The Operator should contain several “functions“ (methods):
    - To connect to the devices (with the controllers it was given as input)
    - Also to disconnect
    - To run a scan (experiment) (there could be multiple of such functions for different scans)
    - To save data
    - For live plotting in a graphical user interface (if you need that)
- View
  - Allows you to interact with the Operator in a graphical user interface (GUI)
  - This has two classes which we call: MonitorWindow (for continuous a live “plotting”) ScanWindow (for performing a scan)

## labphew demonstration

  - Quick demonstration
  - Explaining the layers
  - How would you use it

## Getting your own “copy” to modify

- Repository on github: https://github.com/SanliFaez/labphew
- Forking it
- Cloning it
- Making a conda environment (and why)
- Installing the package
Nomenclature (possibly not purely accurate, but descriptive):
- repository: collection of files being tracked by git versioning software (git helps you maintain different versions, share them, merge them)
- github / gitlab: online services to store a git repository. Sharing between people (or even just different machines) usually goes through the remote copy on github(/lab)
- Cloning a repository: making a “copy” on your local machine that is “linked” to the remote
- Forking a repository: making your own remote “copy” of another project (that is not tracked by the original versioning)
- package: a collection of python files that belong together and can be installed as one (when developing a package it’s usually in a repository, like in our case)
- Having multiple conda environments allows you to install/modify/remove packages without affecting the configuration in other environments and vice versa (note: virtualenv is another solution for python environments)

## Extra bits

## Tips for coding when collaborating

- Always think about someone else having to look through your code In software companies (where code is read much more often than it’s written) this is crucial , but it will help yourself as well when you look at code you’ve written a year ago.
- Use descriptive names for variables and objects.
- Add in-code documentation to classes and their methods. Descipbe what they do. If copy the style used in labphew it is possible to build html documentation from that.
- Comments in code can be good. Even better is to use logging statements (see labphew docs for explanation)

## Important links

- The repository containing the package: https://github.com/SanliFaez/labphew
- Documentation https://labphew.readthedocs.io/en/latest/index.html
- The API documentation doesn’t work yet on readthedocs. You can get a copy from Teams and look at it locally: https://solisservices.sharepoint.com/sites/UtrechtExperimentDesign2020/Shared%20Documents/labphew/html.zip

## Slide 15

I understand you’ll be introduced to git more properly next week.
It is often very confusing to new users. The following slides contain my attempt to explain it

## Versioning with Git, basics

Git can keep track of file-changes in a folder. This folder is then referred to as a repository.
However it does not continuously store all changes. Once you’d like to commit to the changes you’ve made you need to tell git to do so.
To commit file changes you first need to tell git which file-changes you’d like to include. This is called staging.
Once file-changes are staged, they can be committed and become part of the stored history of the repository (“folder”). Each commit should be accompanied with a short message describing what changes are made.
(Note that it is possible to stage file-changes and make more changes to the same file. If you commit at that point, only the staged changes are committed)
You could think of Git as storing a long list of cumulative consecutive commits (“file-changes”) in a folder.
…

## Versioning with Git, branches

…
This main list of commits is usually referred to as the master branch. You can split off from this main branch into another branch. Meaning that these branches have a shared history up to the point where the split happens, and from there on they store their own new commits. This can be very useful when trying something out that you’re not sure yet you want to keep, or when working on one repository with multiple people.
One branch can be merged into another (i.e. the list of commits of one branch are added to another). For example this way you could add the things you’ve been working on in a separate branch into the master branch.
Note that if both branches contain commits that include changes in the same part of the same file, Git can’t decide which to choose and it tells you there’s a merge conflict. It will show the file with both versions of the conflicting parts and you need to pick what you want to keep (i.e. delete sections) .
Solving merge conflict can be a pain and is best to be avoided. It takes a bit of discipline to prevent working on the same file in different branches.
…

## Versioning with Git, remote repository

…
To share code between multiple people (or even multiple computers of one user), it is convenient to store this repository on a server (e.g. website like Github or Gitlab) this is referred to as “remote” whereas your local copy is “local”. The remote becomes the central place for exchanging copies between multiple users/computers and is also referred to as “origin”.
You can push (the new commits of) your local branch to the origin. And you can pull (new commits of) a remote branch to your computer.
A pull can be done in two steps: first fetch (which retrieves the data from the server), followed by a merge of the remote version of the branch into your local version of the branch.
…

## Versioning with Git, tips

Keep your commits small and give them useful messages
When starting “something new” in your code, make a separate branch! It’s easier to keep your master branch clean while you try stuff out on the new branch. Especially if you only work on new files, merging won’t create conflicts
Don’t work on the same file in different branches!
If you’ve made changes in branch A that you also want in branch B, you should merge branch A into B.
In general, but especially when working with multiple people on the same repository, it’s good practice to frequently pull changes from the master branch
Stay aware of what branch you’re working in
It’s a good habit to make sure your code doesn’t crash and commit it before stepping away for a long period. If you come back the next day (or several days later), it’s nice to have it in working order with a commit message you could read back, instead of having to figure out if these changes were valuable or should be trashed.

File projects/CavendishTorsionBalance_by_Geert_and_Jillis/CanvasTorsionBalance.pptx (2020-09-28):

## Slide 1

Cavendish torsion balance

-We want to measure Newton’s gravitational constant (G)
-We want to prove it is possible to do a reasonably complex measurement in the station

Do Cavendish experiment

Comparison with literature value.
Consistency of result.

-Heavy Balls
-Torsion Balance
-Laser, mirrors, optic path
-Camera/optic sensor
-Vibration free space
-Some T control if vibrations low enough
-Vacuum would improve accuracy

See next slide for instructions!

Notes: Go to File > Make a Copy… to make your own canvas
See next slide for instructions

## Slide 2

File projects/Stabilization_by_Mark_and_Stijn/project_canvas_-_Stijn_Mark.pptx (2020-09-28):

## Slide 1

More stable is more better!

The experiments need a certain amount of stability. Two forms:
- eveling the experiment
- Passive (filter out vibration)

- Rigid coupled spring system
- Pully leveling system

Due to the fact that both isolation-material and our stability-material needs space, we decide the size of the experiment (internal size of the box). Also, because of the use of springs, there can only be a certain amount of weight inside of the internal box.

- Large traffic needs to be filtered out
- Once a day, you need to be able to level the experiment

Build for experiments that need stability and need to be level

We make/will have made a rail-system, so multiple experiments can be put within the box.

Springs/gel-packet, wire pully system, accelerometer, plastic box, rails

Specs of the outside box and inside box….

See next slide for instructions!

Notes: Go to File > Make a Copy… to make your own canvas
See next slide for instructions

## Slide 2

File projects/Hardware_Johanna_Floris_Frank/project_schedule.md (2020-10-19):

**Schedule for the  HARDWARE project**

__________________________________________________________________________________________________

**Week 4**

*Monday*
- Collecting the ideas of the subprojects in Teams (private project)
- Talk to the experiment groups
- Define inputs 
- Getting advices on the further process

*Wednesday*
- 12:30 Meeting to brainstorm ideas for the hardware experiment
- Update the 1) Microsoft and 2) with f.e. the new issues from the main repo [subproject_collection](https://git.science.uu.nl/j.lomker/experiment-design-2020/-/blob/master/projects/Hardware_Johanna_Floris_Frank/subproject_collection.md)
- Write brief meeting scheduel for mentro meeting

*Thursday*
- Clarify the missing contents after/during the meeting
- Setup an appointment with mentor Kira and write the **meeting schedule** (discuss exp. and data transfer)

__________________________________________________________________________________________________

**Week 5**

*Monday*

- **Before Monday**: everyone learns about [arduino](https://www.arduino.cc/en/Tutorial/LibraryExamples/MasterReader) and [communication protocols](https://www.arduino.cc/en/reference/SPI), and come up with ideas to implement with arduino on Monday
- Keep on track with transferring info from the [issues](https://git.science.uu.nl/ued2020/experiment-design-2020/-/issues) in the UED repo to our [subproject_collection](https://git.science.uu.nl/j.lomker/experiment-design-2020/-/blob/master/projects/Hardware_Johanna_Floris_Frank/subproject_collection.md)
- **On Monday**, collect the hardware to/and perform simple experiments with the arduino and work towards understanding and developing the communication protocol/tests
- Clarify open questions from the other groups (Software, Power)
- Small adjustments for the [README](https://git.science.uu.nl/j.lomker/experiment-design-2020/-/blob/master/projects/Hardware_Johanna_Floris_Frank/README.md) and [project goal](https://git.science.uu.nl/j.lomker/experiment-design-2020/-/blob/master/projects/Hardware_Johanna_Floris_Frank/project_goals_hardware.md) as well es setting the further [project_schedule](https://git.science.uu.nl/j.lomker/experiment-design-2020/-/blob/master/projects/Hardware_Johanna_Floris_Frank/project_schedule.md). If there is still some time left work on that graph in [subproject_collection](https://git.science.uu.nl/j.lomker/experiment-design-2020/-/blob/master/projects/Hardware_Johanna_Floris_Frank/subproject_collection.md) :)

*Wednesday*
- Meeting with Tijmen & Co

*Thursday*
- **Until Thursday** Issues or in general all the documentation issues that may be left from Monday
- Figure out how to connect several measurments/arduinos with each other.

*Friday/Weekend*
- Updated project goals ready for discussion
- Committed report on context and theory

__________________________________________________________________________________________________

**Week 6**

*Monday*

- Meet at 10:00 to combine the **reports**
- **Submit the Issues**
- Set the week schedule 
- Work on Arduino project/test the new code

*Tuesday*

- Meet at 13:45/14:00 in person and get the skripts done
- Setup appointments for meetings and distribute the rules for schedules etc. via Microsoft Teams
__________________________________________________________________________________________________

**Week 7**

*Friday*

- discussing the feedback
- including (or distribute who does what) the feedback/update the documentation
- splitting the group
- set schedule and ideas for the following week

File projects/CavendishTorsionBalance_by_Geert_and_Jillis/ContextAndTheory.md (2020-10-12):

# Context for the Cavendish balance

In 1680 Isaac Newton published his law for the gravitational force  $`F_g =G \frac{m_1 m_2}{r^2}`$.
The proportionality constant was determined about a century later by Henry Cavendish in a experiment involving a torsion balance and two big masses.
The frequency of the balance yields a value for the torsional spring constant,
such that from the equilibrium position the force between the big masses and the torsion balance can be found.
Current determinations of the gravitational constant use a similar technique, where a torsion balance is influenced by big masses nearby.

# Setup 
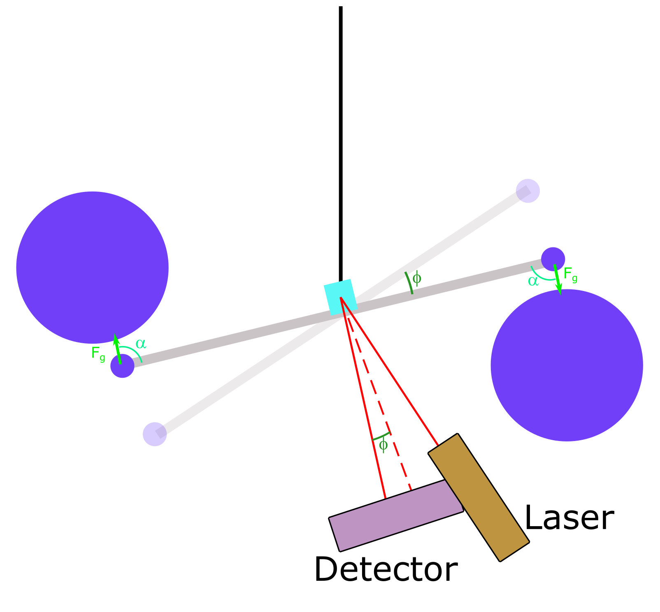
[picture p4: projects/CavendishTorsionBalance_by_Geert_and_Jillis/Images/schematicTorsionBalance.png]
  
    
*Schematic drawing of the setup of the experiment*

The setup of the experiment includes a barbell-like balance (grey and blue) suspended on a (tiny) string (black).
At the ends of the barbell two small masses are afixed, and near them 2 very big masses influence the torsion balance
 due to the gravitational force (light green).
The angle of the gravitational force with the barbell is given as $`\alpha`$ (blue-ish green),
 as this influences the torque the torsion balance experiences.
The balance moves out of equilibrium (partially transparent barbell) by some angle $`\phi`$ (dark green),
 which is registered by a laser-mirror-detector setup.
A laser (brown) shines onte a small mirror positioned in the the middle of the barbell (light blue),
 such that the laserlight (red) is reflected to a light detector (purple) with the same angle as the balance makes with the equilibrium position.
From the position of the light spot on the detector this angle can be calculated.

# Theory
The torsion balance experiences two torques when it is in equilibrium at an angle $`\phi_0`$,
compared to the equilibrium position without the massive balls nearby.
One is based on the gravitational force ($`\tau_g =F_g L \sin\alpha`$), the other is based on the torsion in the wire  ($`\tau_t = -D \phi`$).
Thus the equilibrium position is found as $`\phi_0 = -\frac{F_g L \sin\alpha}{D}`$
However, the balance does not start out in equilibrium and thus will oscilate around $`\phi_0`$.
The rotational equivalent of Newton's second law yields 
```math
I \frac{d^2\phi}{d t^2} = \sum\tau = -D(\phi-\phi_0) - B\frac{d\phi}{dt},
```
here $`B`$ is the damping coefficient for the torsion balance, $`I`$ the moment of inertia.
The solution is a damped oscilation
```math
\phi(t) = A \exp{\left(-\frac{B}{2I}t\right)}\ \sin\left(\sqrt{\omega_0^2-\left(\frac{B}{2I}\right)^2}\right) + \phi_0.
```
Where $`\omega_0 =\sqrt{D/I}`$ is the natural frequency of the balance.

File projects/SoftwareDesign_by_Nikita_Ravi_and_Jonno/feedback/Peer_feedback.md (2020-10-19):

# Reproducibility report

## Experiment/team: 
Software Design/ Ravi, Jonno and Nikita

## Reviewers: 
Maurice, Mark and Jesse

## Report 

### Documentation:

1.	Could you understand the purpose of the experiment? 
- 1st goal. It can be done, but it is easier to do if you already have some background experience.
- 2nd goal. For Psuedo data it works, for real data we were not able to test since there was no real data available.
- 3rd goal. Not achieved.  
**1st goal: I guess once you get it up and running it is intuitive, but a little hard to install.**  
**2nd goal: It also works for the real data. Just trust us :wink:.**  
**3rd goal: Was not asked of us by anyone, although for the AD2 it is basically already implemented and just not shown.**  

2.	Were the safety instructions clear? 
- No safety instructions.  
**Dont blow up your PC and you'll be fine.**  

3.	How helpful is the documentation for reproducing the measurement?
- The documentation is good, there are some minor steps missing which could have been included. This is mainly for setting up the program. The one step we were missing was opening BIMBO. The first time we saw BIMBO we didn't quite know what it meant and what kind of file it was. After looking a bit further we saw that it was a python file so we tried to open it with python which worked.  
**Added meaning of BIMBO to the main README. Also in second README added to run the file in Spyder.**    

4.	Did you get stuck at some point? What extra help did you need to proceed? 
- Some of the lines were missing. No explanation of BIMBO. Took 10 seconds of Ravi's time.
- We tested saving some of the scanning data we obtained with the Arduino, but we were not able to browse for some unclear reason. We didn't know that we could type in the box as well and it took a while for us to find the correct filepath in order to save it. We did this with Ravi's help. For some reason the browse button does work on his PC which is weird.
- Bonus: Getting it working on the Mac took some more time, but this was not tested before. The fact that it worked in the end was very nice. Once it was running it actually worked better than it did on a windows, in the sense that the python code didn't crash when using it multiple times.   
**First point, see above. I think you mean browse with the AD2, but we were not able to reproduce this. For more info see your other feedback file. Nice bonus.**  

5.	Are you guided to reproduce previous measurements? How easily could you navigate through the project documentation?
- Yes we are guided to reproduce measurements, the instrucions for the measurements where very clear. The one change we would make is to add the information about how to find the COM to the same point as filling in the COM. This would make it clearer. 
- Navigation was very easy due to the high number of links.  
**Changed the thing about the COM.**  

6.	What can be improved in the documentation?
- Describing acronyms. Make one big readme rather than 2, because the installation instructions were included in a seperate folder while they could be in the same one. See also [feedback notes](https://git.science.uu.nl/ued2020/experiment-design-2020/-/blob/patch-18/projects/SoftwareDesign_by_Nikita_Ravi_and_Jonno/feedback/FromOthers.md)
- In order to make it more suitable for people without any coding experience include small explanations, e.g. how to comment. The three of us don't quite know how we would start with an additional sensor or any form of contributing. Maybe elaborate on this slightly more under the contributing (mainly a question of us not being very familiar with Arduino), if that is your focus. If you only want contributions from people that fully understand how to encode it then it is fine.  
**Acronyms described. If we merge both READMEs it will get very big. Also, we want to keep general information about the project seperated from info about installing. That's why there is 2, and we think it is a bit clearer. We think our target group should be able to google things like how to comment in Spyder. If you really do not know any programming, we can install the program on your pc and you only have to press a button to start. In the future it would certainly be nice to make the program and executable. We think if you want to contribute, you should already know a little bit as we cannot explain everything. However, people are always free to shoot us a message on teams, we added this to the contributing file.**  

### Measurements:

1.	Can you operate the setup with the provided instructions? 
- Yes after the initial set-up we could easily perform the measurement. Not a real measurement so there is not much that can go wrong.  
**Good.**  

2.	How close were the results you obtain to the previously reported results?
- Results are same, except for different scanning times. 
- Some functionality issues occured such as only being able to run the code once in Python after having to reboot python, maybe this can be solved with pycharm we have not tried this. Or the issue of not being able to browse in our case.   
**For the issue, see the other feedback file.**  

3.	Can you understand and explain the analysis procedure to a third person?
- Yes we could.  
:thumbsup:  

4.	Is the setup robust and safe to operate? 
- Safe to operate. As mentioned before python does a little weird sometimes. There was also a random issue where the pressure measurement didn't work once, issue still not clear.  
**Yeah python is weird.**  

5.	Did you encounter any issues? Could you troubleshoot those without contacting the owners?
- Yes we could solve the issues ourselves. It was a matter of finding the right files. 
- (SPYDER BUG: One time use.)
- We couldn't solve the browse issue ourselves, but if in the instructions it is included that you can type it yourself this would be resolved.
- Random issue with pressure measurement is not clear. Starting the programme again removed this error.  
**Added extra instruction on the browse/textbar. Not sure about that third point. Random things happen and hard to fix if not reproducible. The one time use issues is probably related to Spyder, but not on every pc so hard to actually fix.**   

6.	What part of the measurement procedure did you appreciate most?
- We liked the colours in the graphs. Time well-spend on user interface.
- We also appreciated the fact that the explanations were very clear. The steps were typically easy to follow. The user interface was also nice.    
:fire: :fire: :fire:  

### Interactions:

1.	Could you relate to the stated goal of the project?
- It was not intuitive for people without experience. Some of the set-up can be solved with additional lines of codes.
- Contributing is even less intuitive, we would not know how to add an additional sensor even after we have already used the set-up and have some background knowledge about programming.
- We can relate to wanting to be able to measure something so this goal is very relatable and wanting to make your programme as easy to use as possible is also a good idea.  
**We think our main goals was to make the actual program intuitive and not necessarily the downloading etc. It would be nice to make this into an executable however. Ravi should probably just give away his laptop together with the box. For contributing, the only way to really know how it works is to dig through the code. \#relatable.**  

2.	Which instructions did you need from the owners on top of the written files?
- Instructions on how to install on Mac, there were no instructions for this yet since they hadn't tried it yet. Addition is also in the [feedback notes](https://git.science.uu.nl/ued2020/experiment-design-2020/-/blob/patch-18/projects/SoftwareDesign_by_Nikita_Ravi_and_Jonno/feedback/FromOthers.md).
- Save file would not have worked without the help of Ravi.  
**Added some Mac instructions. We do not know which save file you mean exactly. But for the AD2 browse it was just an unknown bug. For the arduino it is annoying that you cannot see that it is scanning, but we will try to add this. This was however described in the README.**  

3.	Does the experiment accomplish its stated purpose?
- Not entirely not intuitive for people without experience. The measurement itself did work which is nice. I do think it will be interesting to see how well it is going to work once it gets hooked up to all the other systems in the box and real data is provided.  
**Yeah see above for more explanation on the intuitiveness of the program.**  

4.	What do you recommend to the project owners to improve their complete package?
- Add some small additional instructions to clear up the steps that were a bit vague for us. (Also inlcude how to comment something, people without experience would not know how to comment. If you really aim for the programme to be useable by everyone.)
- Add guidelines and information on how to add an additional senser. This is for the contributing section, if this is the aim.
- Enable the user to see when you are scanning.
- Change to Pycharm if this indeed solves the problem of having to reboot SPYDER of having to replug the arduino.
**See above for a reaction on how to comment. For the sensor part, added that you can contact us for more information if you do not have any experience at all. The Arduino scanning thingy will be implemented. Changing to Pycharm would indeed solve some issues probably, but would further complicate the installation. Might do this in the future (next year haha).**  

### General remarks

The reproduction was well explained, all three of us were dreading the software design reproduction at first, but the steps are very clear. We could do the reproduction pretty well.
A job well done on the project. For us the explanation was clear with some small parts missing at some points. A few helpful comments from Ravi helped us through. The fact that it also worked on Mac is pretty nice, without having tested this first. 
We don't know how well it works with actual data, and if it is compatable with the systems used by the other groups.   
:heart: :heart: :heart:

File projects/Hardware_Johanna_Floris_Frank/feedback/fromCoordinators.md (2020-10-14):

# Week 4 discussion

Team Johanna, Frank, Floris

### Feedback on canvas and goals

+ Readme is on a good track, can be more inviting though, folder structure is not so deliberately set
+ How much have you thought of easing the contributions?
+ How are the individual roles defined and arranged?

### Conversation on the progress status

+ be deliberate on assigning tasks
+ separate your demonstration from the service you will provide the grand project
+ focus on the process and not the final product

### on Readme (timestamp: 7/10/2020 ~16h)
⭐⭐⭐☆☆
Motivated me to read further and had at least one link how to get involved, but not all the elements were linked so I quickly got lost. The big picture of the project is there, but i cannot see any detail of where to start learning and what is the latest state.
use of emoji's is 🔥 

### on Instructions (timestamp: 12/10/2020 ~15h)
⭐⭐⭐⭐☆
Very point-by-point. Clear attention for safety considerations. Project seems to consist of 3 different parts which are discussed seperately. The required wiring is sometimes a bit vague. It was easy to find the instructions.

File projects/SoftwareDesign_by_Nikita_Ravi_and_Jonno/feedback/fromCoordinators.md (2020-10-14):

# Week 4 discussion

Team Nikita, Ravi, Jonno

### Feedback on canvas and goals

+ Readme needs some expansion
+ how do you test your achivements? what defines the requirements?
+ why raspberry pi and not digilent? -> already settled on digilent
+ how are the roles defined in the group?

### Conversation on the progress status

+ document you communication with the other groups as much as possible, and make these communications referenceable

### on Readme (timestamp: 7/10/2020 ~17h)
⭐⭐⭐⭐⭐
nice compilation, clearly considerate of the reader and a very good landing page.
I only have a minor suggestion: perhaps also suggest how people can follow up on the existing issues, how to report bugs, and how to share their experiences after going through your guidelines. e.g. have a template issue. 

### on Instructions (timestamp: 12/10/2020 ~15h)
⭐⭐⭐⭐⭐
Instructions are very clear to find. The installation guide is presented step-by-step. Good job! I don't think I have much to add :)

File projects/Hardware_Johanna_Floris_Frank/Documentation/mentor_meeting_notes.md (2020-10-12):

**Utrecht Experiment Design 2020**

**Weekly mentor meeting**
____________________________________________________________________________________________________________
*POP*

*Purpose*: To review your progress and to keep your project on track.

*Outcome(s)*: You know how to proceed with your project.

*Process*: Discuss problems → Get feedback → Review goals → Make new weekly plan
_____________________________________________________________________________________________________________
*General Agenda*

*Review of project goals*

*Review last week’s progress with the project roadmap*
*Review global progress and goals*

*Review of project roadmap*

*Agree on and list the deliverables for following meeting*
*Elaborate on adjustment to your time plan or alternative routes*

*Mentor feedback*

*(What did you learn in your mentor meeting?
What decisions have you made based on the discussions?
Any additional comments...)*
____________________________________________________________________________________________________________
Week no.: 3
PROJECT NAME: HARDWARE

**Agenda**

- Introduce ourselves and goals
- Introduce project and main ideas on communication with the cohort (prepared notebook)
- Discuss the entries from the project canvas
- Get some informations/inspirations to add to our existing questions
- Figure out the best way to collect our notes - microsoft/gitlab - who prepares/pushes what (Readme, project folder) - ...

**Meeting feedback** (1)

- We should use the chance to structure the cohort/grand project (via Teams + clear notes in Gitlab)
- We should write a general concept on how to provide us with information (ID's with notes: data type, for what, response, ... )
- We should define with what kind of data the others should provide us (and the Software-Group)
- Do research on: SPI and USB serial communication
____________________________________________________________________________________________________________
Week no.: 4

**Agenda**
1) Setting the Agenda
2) Opening (Review of project goals)
3) What will we focus on next week?
    - Staying up to date with other groups
    - Working on the grand project (issues, etc.)
    - Working on our individual project
4) What will our individual project be?
5) Agree on and list the deliverables for following meeting
6) Mentor feedback 

**Meeting feedback** (2)
- Digilent is not a viable to serve as a microcontroller, serves no purpose in grand project contribution
- As a group project, test communication protocol(s) between an arduino coupled to a sensor/LED/measurement device and an arduino coupled to computer
- Communication is difficult when the objective is not clear: if the goal is clear, communication is good
- Learning to communicate under stress is part of the learning process
- Make one person responible for taking notes during mentor meeting (and rotate weekly)
____________________________________________________________________________________________________________
Week no.: 5

**Agenda**
1) Evaluation of findings from past week
2) What to do for the deadline on Monday:
    - What to deliver as a first signal and artpiece
    - What to write in the report on context and theory
    - Updating project goals (see also 3))
3) Decide on what we want to further investigate
4) Translate point 3) into a schedule for next week
5) Receive and discuss mentor feedback

**Meeting feedback** (3)
- Make a block diagram for problem treatment
- Include library also in master (for the future: also check the library to see what is possible)
- Thinking about ´converting float into bit
- Piece of code to help us :)

____________________________________________________________________________________________________________
Week no.: 6 (Friday 16:00)

**Agenda**
1) Share notes of the progress from Monday, Tuesday and Thursday
1.1) Discuss problems and find solutions for the data transfer (Digital or Analog)
2) Outline the report for Monday and find a better communication for that  
3) Set Agenda for the next week/Distribute the project files for updates
4) Receive and discuss mentor feedback

**Meeting feedback**
- Focus on serial library	
- No printing inside loops
- Available during the weekend to help with the code **Thank You**

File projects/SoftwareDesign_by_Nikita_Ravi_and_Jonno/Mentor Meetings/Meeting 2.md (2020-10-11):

*Utrecht Experiment Design 2020*

# Weekly mentor meeting 1/10/2020

### POP

+ **Purpose**: To review your progress and to keep your project on track.
+ **Outcome(s)**: Get tips on project goals.
+ **Process**: Discuss project goals → Get feedback → Update files

Week no.: 5
PROJECT NAME: Software Design 

## Meeting feedback (fill after meeting)

+ Link installation in readme
+ Add versions to installation guide
+ Add multiple platforms (linux windows etc) to installation guide

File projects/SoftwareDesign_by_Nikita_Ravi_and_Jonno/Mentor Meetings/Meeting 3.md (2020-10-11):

*Utrecht Experiment Design 2020*

# Weekly mentor meeting 8/10/2020

### POP

+ **Purpose**: To review your progress and to keep your project on track.
+ **Outcome(s)**: Get tips installation guide
+ **Process**: Discuss README → Get feedback → Update files

Week no.: 5
PROJECT NAME: Software Design 

## Meeting feedback (fill after meeting)

+ All seems good. Meet in two weeks

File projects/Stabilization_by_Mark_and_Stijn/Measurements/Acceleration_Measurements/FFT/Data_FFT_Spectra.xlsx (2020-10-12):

Frequency | Amplitude Schuim/blok | Amplitude Schuim/Blok met veer | Amplitude Schuim/Blok met veer en schuim | Amplitude Schuim/Blok met schuim | Amplitude Playground/Blok
20 | 33.0 | 70.0 | 70.0 | 52.4 | 42.8
25 | 31.6 | 60.8 | 70.0 | 47.8 | 32.2
30 | 70.0 | 52.2 | 60.8 | 47.8 | 50.2
35 | 40.2 | 53.6 | 49.4 | 53.8 | 33.2
40 | 35.0 | 59.4 | 56.0 | 50.2 | 28.2
45 | 29.8 | 60.4 | 56.2 | 46.4 | 28.2
50 | 22.4 | 49.8 | 49.0 | 42.4 | 25.6
55 | 19.6 | 37.4 | 34.4 | 39.6 | 24.2
60 | 22.6 | 42.2 | 36.6 | 43.2 | 25.0
65 | 25.2 | 46.8 | 40.6 | 48.4 | 27.8
70 | 26.8 | 50.4 | 45.2 | 51.6 | 29.0
75 | 29.2 | 54.6 | 48.4 | 51.8 | 29.6
80 | 30.2 | 56.6 | 52.0 | 53.4 | 30.8
85 | 31.6 | 59.0 | 55.0 | 53.2 | 32.4
90 | 32.4 | 70.0 | 56.0 | 54.0 | 34.2
95 | 33.0 | 70.0 | 58.4 | 56.2 | 35.0
100 | 33.4 | 70.0 | 70.0 | 56.2 | 35.6

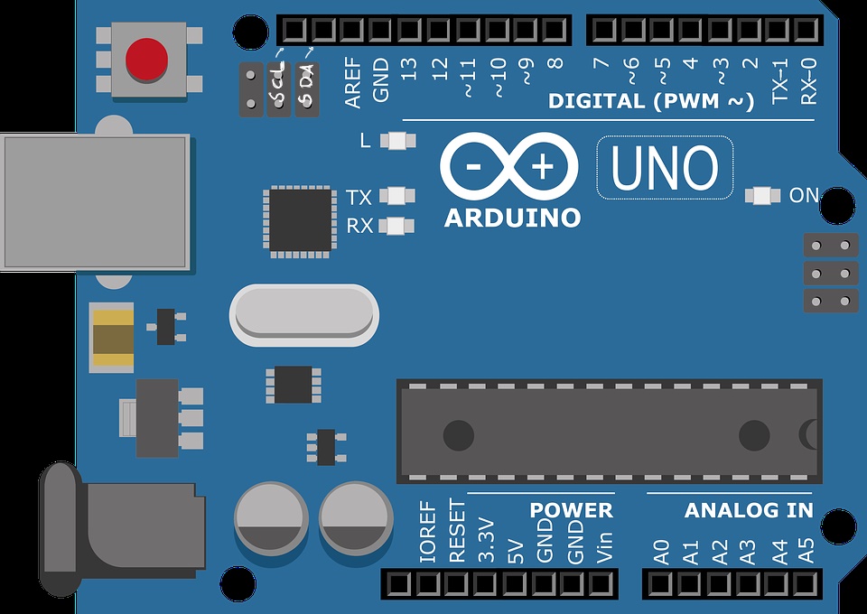
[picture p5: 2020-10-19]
projects/Hardware_Johanna_Floris_Frank/Documentation/images/Inkedarduino_LI.jpg

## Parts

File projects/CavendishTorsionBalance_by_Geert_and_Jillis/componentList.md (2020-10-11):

| component | info | status |
| ------ | ------ | ------ |
| servo/stepper motors | 2 servo's, 5V, ~ 1000mA max draw | bought |
| PLA filament | for printing parts | bought |
| balls | 2 large, 2 small | (small) bought, (big) borrowed from university |
| camera/sensor ?| for vibrations in the other axes (bigger range) | not used |
| other optical components?| for vibrations in the other axes (bigger range) | not used |
| parts for barbell  | in cooperation with Pascal | finished |
| container for experiment | in consultation with team vibration | not present | 
| output sensor to digital converter for modular box | in consultation with team hardware | unknown |
| output sensor to digital converter for temporary setup | currently using Analog Discovery 2 | present |
| servo controller for temporary setup | currently using arduino with an additional power supply |set up|
| servo control via modular system | in consultation with team hardware / data | unknown |

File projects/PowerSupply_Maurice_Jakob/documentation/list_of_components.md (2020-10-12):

# List of components

### Power source

| Component | Models | Remarks |
| ------ | ------ | ------ |
| Charger for lead-acid | [simple](https://www.conrad.nl/p/voltcraft-loodaccu-lader-bc-1001-6-v-12-v-laadstroom-max-1-a-1406342) | - |
| USB charger | [max 3A](https://www.conrad.nl/p/ansmann-home-charger-130q-1001-0099-usb-oplader-thuis-uitgangsstroom-max-3000-ma-1-x-usb-30-bus-a-2227123) | - |

### Storage

| Component | Models | Remarks |
| ------ | ------ | ------ |
| Power bank | [powerbank](https://www.conrad.nl/p/anker-powercore-26800-powerbank-li-ion-26800-mah-a1277011-1672847) | - |
| 12V lead battery | [12 aH](https://www.conrad.nl/p/conrad-energy-12-v-12-ah-loodaccu-12-v-12-ah-loodvlies-agm-b-x-h-x-d-151-x-95-x-98-mm-kabelschoen-635-mm-onderhouds-250916) | - |
| 20A fuse | 2x [holder](https://www.conrad.nl/p/tru-components-tc-r3-32b1-zekeringhouder-geschikt-voor-buiszekering-63-x-32-mm-20-a-32-vdc-1-stuks-1587916) + 6x [fuse](https://www.conrad.nl/p/eska-140031-buiszekering-x-l-63-mm-x-32-mm-20-a-32-v-snel-f-inhoud-1-stuks-527658) | - |

### Interfacing components

| Component | Models | Remarks |
| ------ | ------ | ------ |
| Inverter | [150W](https://www.conrad.nl/p/voltcraft-msw-150-12-g-converter-150-w-12-vdc-230-vac-past-in-bekerhouder-1277756)| - |
| Load switch and monitoring | - | assemble with Dante |  

### Cables

| Component | Models | Remarks |
| ------ | ------ | ------ |
| USB type A cable | 2x [charger <-> powerbank](https://www.conrad.nl/p/digitus-usb-20-aansluitkabel-1x-usb-a-20-stekker-1x-usb-a-20-stekker-100-m-zwart-678038), cable from charger to powerbank and  one for DC/DC converter to powerbank | |
| USB splitter | [power splitter](https://www.conrad.nl/p/logilink-ua0138-4-poorten-usb-20-hub-groen-986336) for multiple arduinos | |
| power lines 12V | | cables for 12V battery and load-switch |
| USB cable to connect powerbank and Hub | [this](https://www.conrad.nl/p/manhattan-usb-20-verlengkabel-1x-usb-a-20-stekker-1x-usb-20-bus-a-100-m-zwart-folie-afscherming-ul-gecertificee-1592188) | |

### Solar

| Component | Models | Remarks | 
| ------ | ------ | ------ |
| cell | cell | cell |
| Solar panel |  [solar outlet](https://www.solar-outlet.nl/q-cells-duo-320-black.html) + [set MC4 connector](https://www.solar-outlet.nl/mc4-connector-set.html) | - |
| Charging controller | [solar CC](https://www.conrad.nl/p/steca-solarix-prs-2020-solar-laadregelaar-serie-12-v-24-v-20-a-110704) | 48V to 12V converter and charge controller for lead-acid battery |
| DC/DC converter | [converter](https://www.conrad.nl/p/dcdc-omvormers-mean-well-sd-15a-5-3-a-1292699) | 12V to 5V converter |

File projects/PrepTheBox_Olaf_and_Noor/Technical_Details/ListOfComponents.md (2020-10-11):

| Component | Information | Status Component |
| ------ | ------ | ------ |
| Plate to separate the module room and the experiment chamber | . | Placed in box |
| Ventilation | To cool the insides down | Not obtained yet |
| Kit | To make the insides watertight | Replaced by Dukttape |
| Rail-suspention system | To hang the modules in | Not obtained yet |
| Screws to fasten all the sides | Not all sides are fastened yet | Replaced by Dukttape |
| Brakes | To keep the box from rolling away | Obsolete |
| Wheels adjustable in height | To make the box more leveled | Support instead of wheels placed under the box |
| Isolation material | To keep the insides on temperature | Obsolete |

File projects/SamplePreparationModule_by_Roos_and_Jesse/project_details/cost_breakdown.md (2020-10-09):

|material|cost(€)|
|--------|-------|
|wood| 34.18|
|fan| free (recycled from old computer)|
|plexiglass| from Dante (would have cost 41.99)|
|polyurathane coating| 0.75 (thrifted)|
|paint| free (used leftover) |
|rail| 3.29 |
|slat| 4.59 |
|ductape| 2.69 |
|retractable pipe| 3.29 |
|pvc pipe| 2.39 |

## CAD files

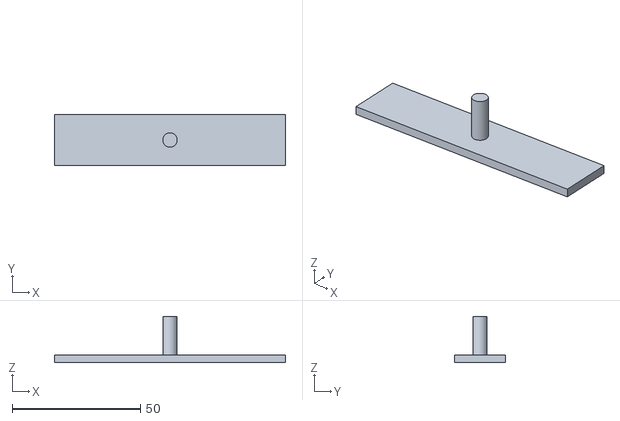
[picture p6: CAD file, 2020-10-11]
projects/CavendishTorsionBalance_by_Geert_and_Jillis/Design/Brace.stl
90.0 x 20.0 x 18.0

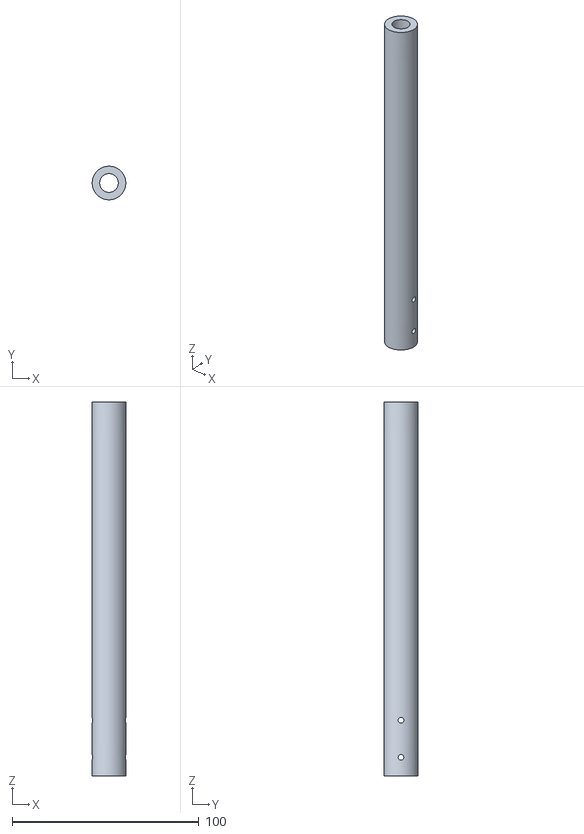
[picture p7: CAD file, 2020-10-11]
projects/CavendishTorsionBalance_by_Geert_and_Jillis/Design/Tube_1.stl
18.0 x 18.0 x 200.0

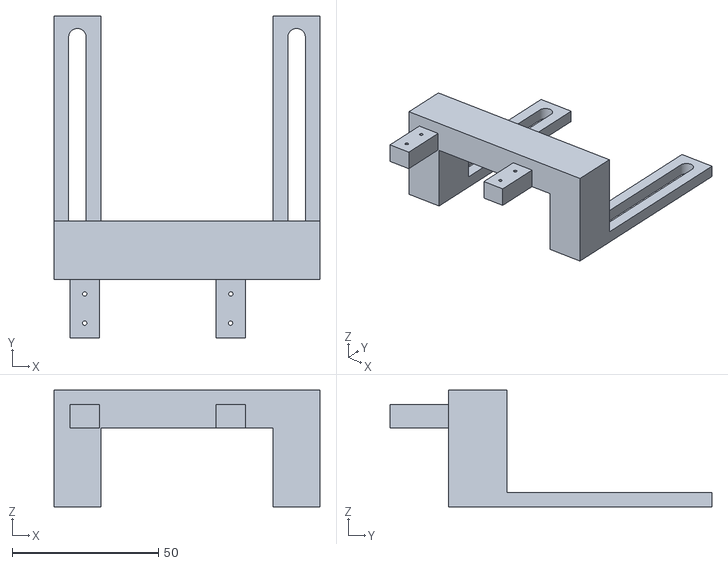
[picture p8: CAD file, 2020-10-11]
projects/CavendishTorsionBalance_by_Geert_and_Jillis/Design/Motor_module.stl
91.0 x 110.0 x 40.0

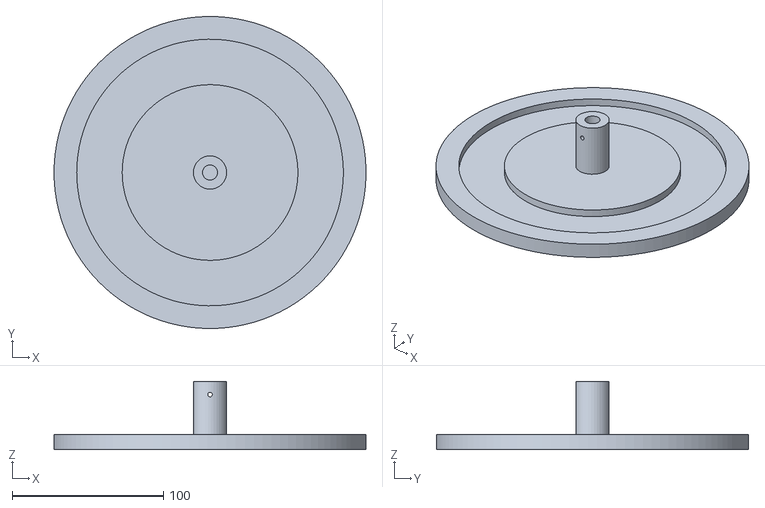
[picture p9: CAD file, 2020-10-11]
projects/CavendishTorsionBalance_by_Geert_and_Jillis/Design/Ground_Plate_V2.stl
206.0 x 206.0 x 45.0

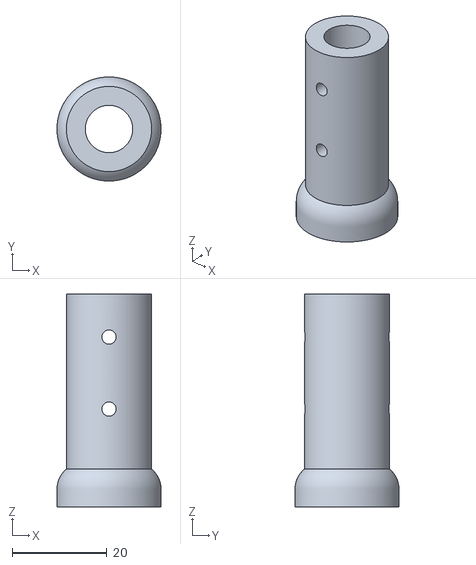
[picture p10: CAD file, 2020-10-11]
projects/CavendishTorsionBalance_by_Geert_and_Jillis/Design/Tube_extension.stl
22.0 x 22.0 x 45.0

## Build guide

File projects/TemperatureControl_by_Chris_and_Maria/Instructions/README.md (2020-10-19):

Here you will find the instructions on how to install Arduino in your computer, make the circuit on your own and make it work! If you find something that it is not clear please inform us and we will fix it!

Update: We have uploaded updated instruction BUT they are not completed! This is because we are still working on the project.

Now the circuit is soldered as it was mentioned in peerfeedback, so you will not be able to reproduce it with these materials as you will do this without being soldered!

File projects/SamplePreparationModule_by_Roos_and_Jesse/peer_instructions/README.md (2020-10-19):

##### Welcome to the reproduction directory!

In this section we will try and guide you through the procedure of how the preparation module was tested. Before we tell you more about how to test everything we ask that you first read the [instructions](https://git.science.uu.nl/ued2020/experiment-design-2020/-/blob/master/projects/SamplePreparationModule_by_Roos_and_Jesse/peer_instructions/instructions.md). In the [instructions](https://git.science.uu.nl/ued2020/experiment-design-2020/-/blob/master/projects/SamplePreparationModule_by_Roos_and_Jesse/peer_instructions/instructions.md) you are able to find some contact information when you want to perform experiments on campus. It includes [safety instructions](https://git.science.uu.nl/ued2020/experiment-design-2020/-/blob/master/projects/SamplePreparationModule_by_Roos_and_Jesse/peer_instructions/instructions.md) which must read before performing any testing. Finally, it includes instructions on how to use a Finn pipet if you are unfamiliar on how to use this.

The information that will be provided below is centred around testing the sample preparation module. Additional information about how the sample preparation module was build can be found in the [building process](https://git.science.uu.nl/ued2020/experiment-design-2020/-/blob/master/projects/SamplePreparationModule_by_Roos_and_Jesse/project_details/building_progress.md). We also have a [cost breakdown](https://git.science.uu.nl/ued2020/experiment-design-2020/-/blob/master/projects/SamplePreparationModule_by_Roos_and_Jesse/project_details/cost_breakdown.md) if you are interested in the total price of building a fumehood yourself. The [goal of the project](https://git.science.uu.nl/ued2020/experiment-design-2020/-/blob/master/projects/SamplePreparationModule_by_Roos_and_Jesse/project_details/project_goals.md) was to building a fumehood that is ventilated and chemically resistant. We will now bring you through the steps of how to perform this testing. 

Have you read the [instructions](https://git.science.uu.nl/ued2020/experiment-design-2020/-/blob/master/projects/SamplePreparationModule_by_Roos_and_Jesse/peer_instructions/instructions.md)? If not, please do so. Otherwise feel free to continue. We have split up the testing process in two components.

### Coating testing

In order to perform any tests of the coating you will first need access to a lab equipped to work with acids. If you have connections to such a lab you can also go there. If not you can contact Jesper Moes (j.r.moes@uu.nl) and make an appointment.
In order to perform the testing we have supplied you with an additional piece of wood that is also coated with the polyurethane coating. This is supplied with the box. The side that has our test results on it has been coated and the left side of the wood is for the reproduction of our test. 
Before you go into the lab make sure that you are wearing a lab coat and safety goggles as instructed in the [safety instructions](https://git.science.uu.nl/ued2020/experiment-design-2020/-/blob/master/projects/SamplePreparationModule_by_Roos_and_Jesse/peer_instructions/instructions.md).

When you have to clean up there are four waste containers. Acids, anorganic substances, organic halogen rich, organic halogen poor.
While working with acids you have to dispose your waste in the acids container, while working with acetone, ethanol or toluene you have to dispose your waste in organic halogen poor.

#### Testing with nitric acid:
- Read the entire instructions first so you can prepare all glass work and tools you need. You might also want to label your glass work so you know what it contains.
- Fill a glass beaker with 10ml nitric acid.
- Make 10%, 25% and 50% diluted concentrations. This is done by adding demi water.
1. For 10% add 9ml demi water to a second glass beaker using an Finn Pipet. Add 1ml, using an Finn pipet, of 100% nitric acid.
2. For 25% add 7.5ml demi water to a third glass beaker using an Finn Pipet. Add 2.5ml, using an Finn pipet, of 100% nitric acid.
3. For 50% add 5ml demiwater to a fourth glass beaker using an Finn Pipet. Add 5ml, using an Finn pipet, of 100% nitric acid.
- Before pipeting acid concentrations onto the testing wood, you want to stir it with a glass pasteur pipet, to prevent any outlying high acid concentrations.
- Indicate what you are testing on the wood using a pencil.
- Pipet approximately 1ml of acid onto the wood next to your indication, use a different pasteur pipet for each acid. You are using a pasteur pipet which does not allow for a quantative measurement.
- Leave every concentration on the wood for 5 minutes before removing it with an pasteur pipet and disposing it in an additional 'waste' glass beaker.
- There will be a small residual amount of acid left so you can pipet a little bit of water on the spot as well and dispose this in the same 'waste beaker'.
- Wipe the area you have tested with a paper tissue to remove any of the already diluted acid or water that may still be left on the wood. 
- Empty your glass beakers and waste in the designated container. Clean them using demiwater, ethanol and alcohol. If you don't have any lab experience ask the supervisor if he can help you.

#### Testing with hydrochloric acid:
- Read the entire instructions first so you can prepare all glass work and tools you need. You might also want to label your glass work so you know what it contains.
- Fill a glass beaker with 10ml hydrochloric acid.
- Make 10%, 25% and 50% diluted concentrations. This is done by adding demi water.
1. For 10% add 9ml demi water to a second glass beaker using an Finn Pipet. Add 1ml, using an Finn pipet, of 100% hydrochloric acid.
2. For 25% add 7.5ml demi water to a third glass beaker using an Finn Pipet. Add 2.5ml, using an Finn pipet, of 100% hydrochloric acid.
3. For 50% add 5ml demiwater to a fourth glass beaker using an Finn Pipet. Add 5ml, using an Finn pipet, of 100% hydrochloric acid.
- Before pipeting acid concentrations onto the testing wood, you want to stir it with a glass pasteur pipet, to prevent any outlying high acid concentrations.
- Indicate what you are testing on the wood using a pencil.
- Pipet approximately 0.5-1ml of acid onto the wood next to your indication, use a different pasteur pipet for each acid. You are using a pasteur pipet which does not allow for a quantative measurement.
- Leave every concentration on the wood for 5 minutes before removing it with an pasteur pipet and disposing it in an additional 'waste' glass beaker.
- There will be a small residual amount of acid left so you can pipet a little bit of water on the spot as well and dispose this in the same 'waste beaker'.
- Wipe the area you have tested with a paper tissue to remove any of the already diluted acid or water that may still be left on the wood. 
- Empty your glass beakers and waste in the designated container. Clean them using demiwater, ethanol and alcohol. If you don't have any lab experience ask the supervisor if he can help you.

#### Testing with ethanol and acetone:
- Read the entire instructions first so you can prepare all glass work and tools you need. You might also want to label your glass work so you know what it contains.
- Fill two glass beaker with approximately 2ml ethanol and acetone repectively.
- Indicate the region on the wood where you are going to test.
- Using a pasteur pipet, pipet approximately 0.5-1ml ethanol and acetone on the wood regions you indicated in the previous step.
- Leave it for 5 minutes, before removing it with an pasteur pipet and disposing it in an additional 'waste' glass beaker.
- Wipe the wood with a paper tissue. 
- clean your glass work and your waste container, in the designated container. If you don't have any lab experience ask the supervisor if he can help you.

#### Testing with Aqua Regia:
- Ask for assistance from a lab supervisor. In our case Naud van Bunningen (a.j.vanbunningen@uu.nl) was present. 
- You will need two glass beakers: one containing 5ml of hydrochloric acid and 1 containing 1 ml of nitric acid.
- Indicate a region on the wood where you want to test.
- Ask supervisor to pipet 0.5-1ml aqua regia onto the wood in the region you have indicated.
- Leave it for five minutes before asking the supervisor to remove it.
- Clean with a bit of demiwater before wiping with a paper tissue.
- Cleaning requires extra safety gloves. Ask supervisor for help.

#### Testing with Toluene:
- Read the entire instructions first so you can prepare all glass work and tools you need. You might also want to label your glass work so you know what it contains.
- Toluene evaporates very quickly, do not inhale fumes, you will need an beaker glass that you can close completely. Experiment has to be peformed in a fumehood.
- Fill beaker glass with lid with approximately 2 ml of toluene and immediately close the lid.
- Indicate where you want to pipet your toluene.
- Use a pasteur pipet to pipet 0.5-1ml toluene into the region you have indicated. Close the beaker glass immediately afterwards.
- Close the fumehood and leave it for 5 minutes.
- If not all toluene has evaporated you can put it back in the glas beaker with lid before wiping it with a paper tissue.
- Clean your glass work and deposit your toluene in the designated container. If you have no lab experience you can ask the supervisor to help you.

In addition to these step-by-step procedures you can find our test results and steps in the [coating testing file](https://git.science.uu.nl/ued2020/experiment-design-2020/-/blob/master/projects/SamplePreparationModule_by_Roos_and_Jesse/Testing/testing_coating.md)

Directly after having performed these tests one can see which chemicals cause any visual damage to the coating. Since the chemicals may have dissolved slightly into the coating we stress that you do not touch any of these areas yet, since this may still be harmful. Therefore there will be a second test that is done, which is not an exact measure. After 24 hours feel each area to see if there is any none visible damage. Sometimes it might be very difficult to feel that is why these results are not exact. 

### Airflow testing
In order to do the airflow testing you have to contact Pascal Koopman (p.koopman@uu.nl) he has the anemometers. Ask for one from [travel&co](https://git.science.uu.nl/ued2020/experiment-design-2020/-/blob/master/projects/SamplePreparationModule_by_Roos_and_Jesse/Photos/Travel_co_anemometer.jpeg), one from [testo](https://git.science.uu.nl/ued2020/experiment-design-2020/-/blob/master/projects/SamplePreparationModule_by_Roos_and_Jesse/Photos/testo_anemometer.jpeg) and a [kaindl windmaster 2](https://git.science.uu.nl/ued2020/experiment-design-2020/-/blob/master/projects/SamplePreparationModule_by_Roos_and_Jesse/Photos/kaindl_anemometer.jpeg). 
In our measurements we found the testo anemometer to be the most accurate, you can see if you obtain the same result.
Attach the fan to the battery as you have read in the [instructions](https://git.science.uu.nl/ued2020/experiment-design-2020/-/blob/master/projects/SamplePreparationModule_by_Roos_and_Jesse/peer_instructions/instructions.md).
There are several locations of the fumehood that you will have to measure:
- To find if there is any 'background' you first measure the room. (Here we found the highest accuracy with the Testo anemometer)
- The sides of the top window and the front window.
- The end of the PVC pipe at the top of the box. This is measured with the sash open to enable a good airflow.
- In front of the sash window while it is fully opened. Keep the anemometer in the middle.
- In front of the sash window when it is almost fully closed. Leave approximately 0.5 mm. Hold the anemometer in the middle again.
- In the middle of the box, around 24 cm from each side and 13 cm elevated. (this is with the sash window open)
- In the right middle of the box, around 12 cm from the right side of the box and 13 cm elevated. (Sash is open.)
- In the left middle of the box, around 12 cm from the left side of the box and 13 cm elevated. (Sash is open.)
- Right below the fan inside the box. This is measured with the sash open.
- At the side of the fan inside the box, same height as the fan but now located 2cm from the side of the fan without changing the height. This is measured with the sash open.

Comparing the results can be done by opening the [airflow testing file](https://git.science.uu.nl/ued2020/experiment-design-2020/-/blob/master/projects/SamplePreparationModule_by_Roos_and_Jesse/Testing/testing_airflow.md). This also contains a comparison with professional fumehood wind speeds.

#### Good luck!

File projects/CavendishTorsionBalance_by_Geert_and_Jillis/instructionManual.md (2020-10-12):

This document assumes the reader has read the [context and theory](ContextAndTheory.md) file, and thus knows roughly the aim of the experiment and has some idea of the setup.

**The setup is placed on a optical table. This is to minimize the amount of interference of vibrations in the environment. To preserve your sanity, do not touch the optical table (while measuring, nor at any other moment) unless your are sure you need to realign the laser.**

# Setup
The setup consists of 3 main parts; the torsion balance, the control mechanism and the detection suite.

## Torsion balance
The torsion balance consists of a round baseplate, a turningtable with holders for large balls, an insulated and grounded holder for the torsion balance and the torsion balance itself. The holder can be rotated at the base for finetuning. In the holder a Halter(or barbell) is suspended by a thin rectangular wire. This can be adjusted in height and angle at the top. **If it is necessary to adjust with this part of the setup, please be extremely careful.** It is a quite delicate piece of equipment, the wire is valuable and easily broken. During the measurement it should not be necessary to interface directly with any of these components torsion balance. 

## Control mechanism
The setup is controlled by a continuous servo attached to an Arduino Due.
The Arduino needs an external power source, as the servo needs a higher voltage than USB can provide. It is necessary to first connect the power source and **then** connect the USB to the Arduino. Otherwise the wrong power supply is used. On the Arduino a [program](Arduino_Controll) can be run to control the position of the turningtable with the big masses.

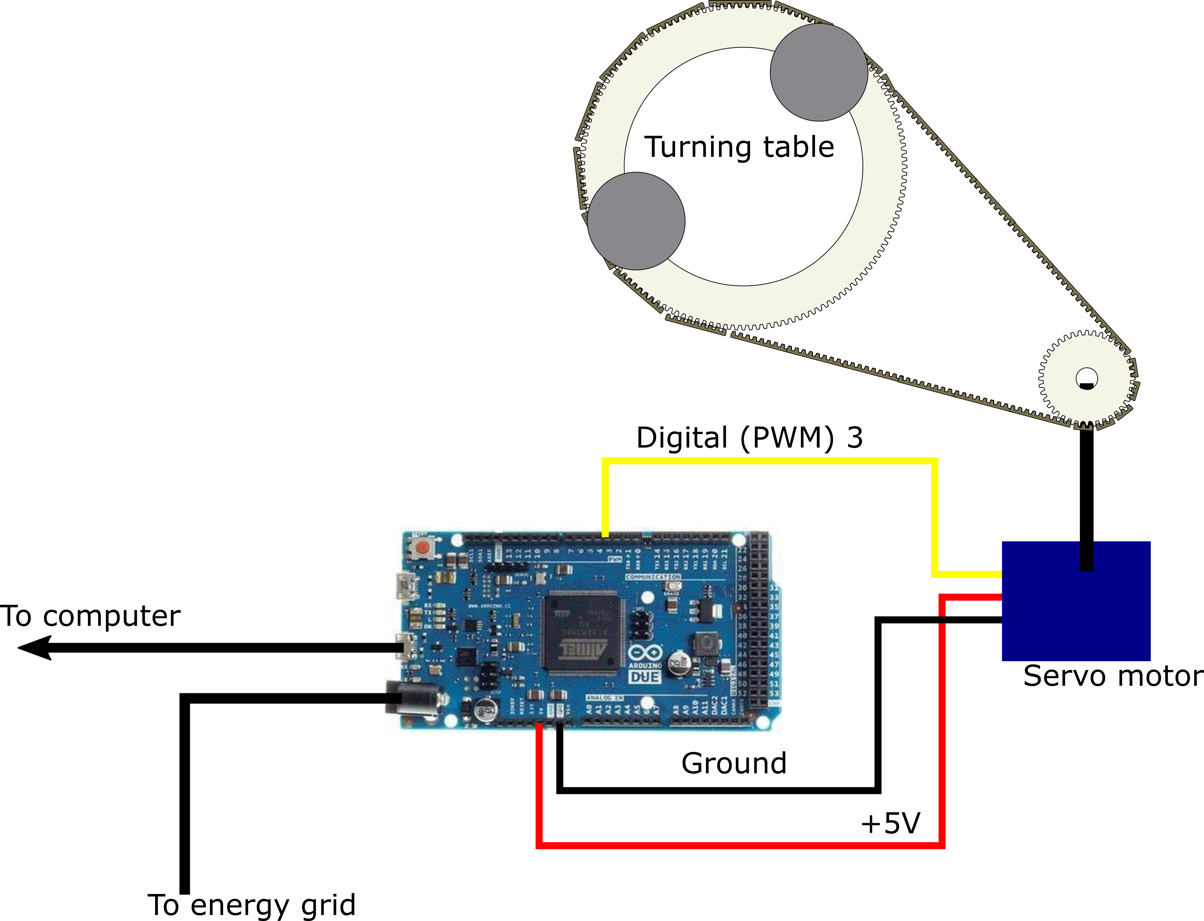
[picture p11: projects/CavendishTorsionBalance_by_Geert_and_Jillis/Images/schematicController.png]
 

## Detection suite
The detection suite comprises a laser, a lightposition detector, a modulator and amplifier and the Digilent Analog Discovery 2. 
The laser and detector are connected to the modulator to isolate the signal from other light effects which might be picked up by the detector. 
The outputs of the modulator are connected to the oscilloscope channels on the Digilent Analog Discovery 2.
To read out the signal of the oscilloscope it is necessary to download either the [Waveforms package from Digilent](https://store.digilentinc.com/waveforms-download-only/) or the package that is being written by the [Software group](../SoftwareDesign_by_Nikita_Ravi_and_Jonno). The modulator outputs two voltages which are based on the position of the brightest spot on the detector.

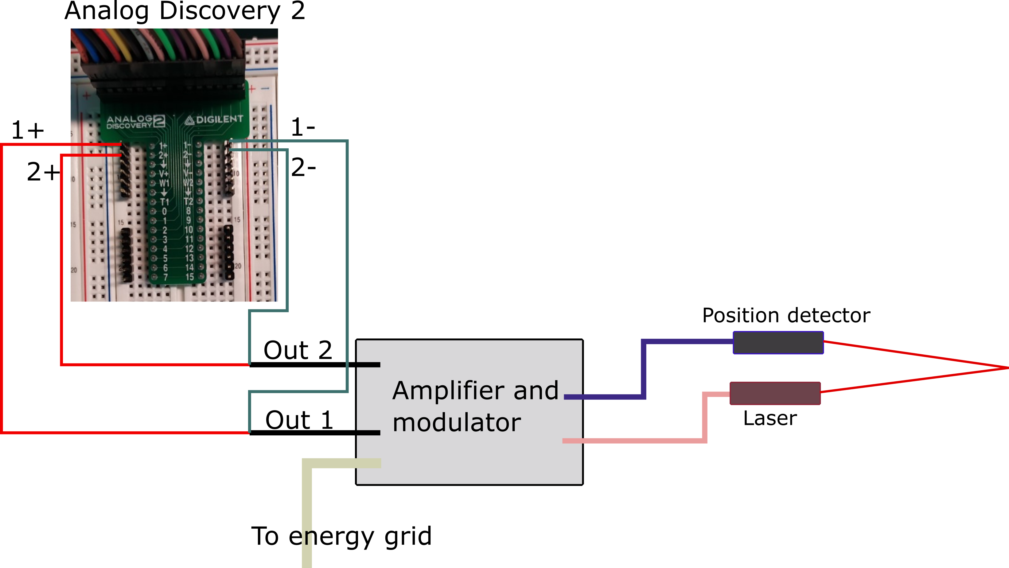
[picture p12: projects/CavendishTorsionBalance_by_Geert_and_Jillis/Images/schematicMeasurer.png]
 

## measurements of the setup
| part | measure |
| ------ | ------ |
| small balls | 6.33 g and 6.29 g |
| big balls | 1214.0 g and 1214.8 g |
| full barbell (including mirror, balls, rod, connector to wire, ...) | 31.7 g |
| barbell length | (12.0 ± 0.2) cm |
| diameter big balls | 5.09 cm |
| Thickness box | (3.0 ± 0.1) cm |
| distance box - dectector | (25.0 ± 0.5) cm | 
 
Other uncertainties are 0.5 times the last digit given.

# Method
To find a value for G it is needed to measure 2 values of the rest angle $`\phi_0`$,
 one where the balls are both clockwise close to the balance and one where the balls are counterclockwise close to the balance.
From the difference in these equilibrium positions the torque of the gravitational force can be inferred. The torsion constant is determined by measuring the oscillation frequency of the halter.  
For this several steps need to be taken;
1. Align the reflected laser onto the detector (if not already done)
2. Make sure the big masses/balls are in the center between the two extreme positions
3. Connect both the Arduino and the Analog Discovery 2 to a computer
4. Start and setup the [Waveforms software](WaveformsSetup.md) and the [Arduino program](Arduino_Controll)
5. Move the balls to one of the extremes using the Arduino
6. Start a new measurement in the Waveforms software
7. Wait for about one hour
8. Store the data from the Waveforms software
9. Move the balls to the opposite extreme
10. Repeat steps 6. through 9. several times
11. Fit the model given in the [theory](ContextAndTheory.md) to the data collected. It might be beneficial to divide the two output channels to lower the noise in the signal.

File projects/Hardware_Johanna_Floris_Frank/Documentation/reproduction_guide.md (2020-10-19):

**General remarks**

- Since this projects is basically just connecting some Arduino's with some wires and running sketches on there, there are no special safety concerns inherent to the set-up
- Necesarry items are all found in our project box (along with a few redundant items you can leave in peace).

**Hardware required**

- Two Arduino UNO (other Arduino types would work, but the connection pins will be different than described here) with USB connecting cables



- Breadboard (For absolute certainty: to connect two wires, they must be placed in the same row of the breadboard)
- GybMep BME/BMP280 sensor

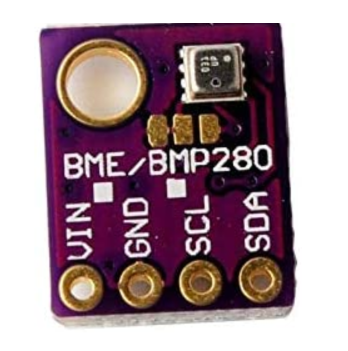
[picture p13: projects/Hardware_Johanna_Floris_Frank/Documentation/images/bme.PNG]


- Connecting wires
- PC with USB port (preferably 2, but one is also possible)
- Multimeter
- Two banana connector electric cables, two alligator connection clips

- If you do not receive a signal following the instructions, it is possible this is due to a non-function wire. This can be checked using a multimeter with two cables with alligator clip connections attached. With the multimeter in diode mode and the clips not in contact with each other, the multimeter should read a voltage of typically 2-3 V. Clamping each connecting end of the wire in one of the clips, the voltage difference should vanish (like what happens if you directly hold the clamps together). If the voltage doesn't drop, the wire is broken, which you can then throw in the bin.

**Setting up Arduino software**

- If you haven't already, download the Arduino [IDE](https://www.arduino.cc/en/Main/Software) software for your relevant operating system
- Open the Arduino program. Within the program, open the library manager **(sketch -> include library -> manage library, or press Ctrl+Shift+I)**, look for the **Adafruit_BME280 library**
- Install the Adafruit_BME280 library. The program should request to also install other libraries necessary for the Adafruit_BME280 library to function. Accept this request.
- Check if the **Wire, SoftwareSerial and Adafruit_Sensor libraries** are installed. The first two should be installed by default, the last one should be included if you have correctly followed the previous step. If any of them are, for some reason, not yet installed, do so.
- The links in this document link to Arduino sketches directly. In our experience, Arduino sketches need to be saved in a separate folder with the same name as the sketch itself (except for the .ino format denoter) for them to work.

**Experimental setup and instructions**

*Running the sketches*
- verify the code (the v on the top left) and upload to the relevant Arduino (the arrow next to the verify button). The USB port to which the program is uploaded can be changed under tools -> port, and checked on the bottom right.
- Read out the master/slave by opening the Serial monitor under tools, or **press Ctrl + Shift + M** (be sure you select the correct baud rate, which is given in the Arduino sketch as e.g. as an argument of the Serial.begin() functionality, typically set at 9600)
- **Take care** to upload the correct script with the correct COM

*Single master-single slave text-based I2C communication via analog ports, Arduino basics*
- Connect both Arduino's  to your PC (on seperarte USB ports) using the USB cables. Make sure you know the adress of the USB port each Arduino is connected to
- Pick one Arduino as the slave, the other as the master
- Connect the (analog) ground pins and the analog A4 and A5 pins on one Arduino to the same pins on the other Arduino
- Open the [master sketch](https://git.science.uu.nl/ued2020/experiment-design-2020/-/blob/master/projects/Hardware_Johanna_Floris_Frank/Arduino_code/master_reader.io.ino) and the [slave sketch](https://git.science.uu.nl/ued2020/experiment-design-2020/-/blob/master/projects/Hardware_Johanna_Floris_Frank/Arduino_code/slave_reader.ino)
- Feel free to change around the delay in the master sketch or the print message in the slave sketch. After updating, the altered sketch (naturally) has to be verified and uploaded to the corresponding Arduino again.
- If you only have a single USB port, connect the 5V power output pin on your master Arduino with the Vin pin on the slave Arduino. Use the one USB port to first upload the slave sketch, and then connect the master to the USB port to power it, upload the master sketch and read out the master output.
- Once per loop, the master output should write the string "hello".  
- If this works, proceed to the next experiment.

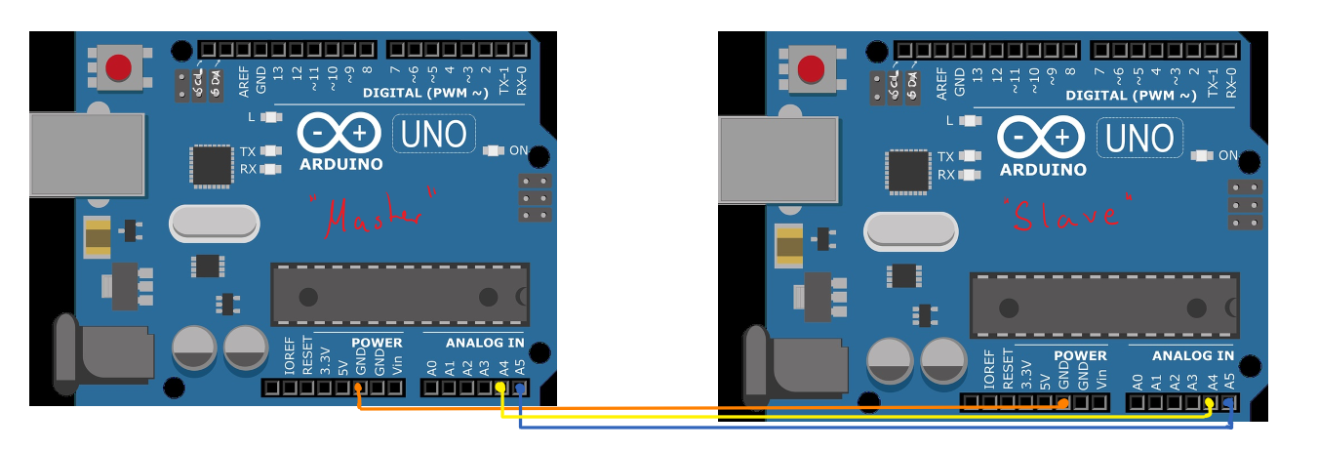
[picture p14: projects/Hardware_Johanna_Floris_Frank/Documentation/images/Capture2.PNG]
 

*Read out the BME/BMP280 Sensor*
- Connect the *BME sensor* VIN and GND to the corresponding analog Arduino pins (5V, Ground)
- Connect the SCL and SDA from the sensor to the corresponding pins from the Aurduino
- Open the [BME sketch](https://git.science.uu.nl/experiment-design-2020/-/tree/master/projects/Hardware_Johanna_Floris_Frank/Arduino_code/BME.ino)
- As before, read the Arduino output, which once per loop should give normal values for temperature, pressure, approximate altitude and humidity.
- If this works, proceed to the next experiment.

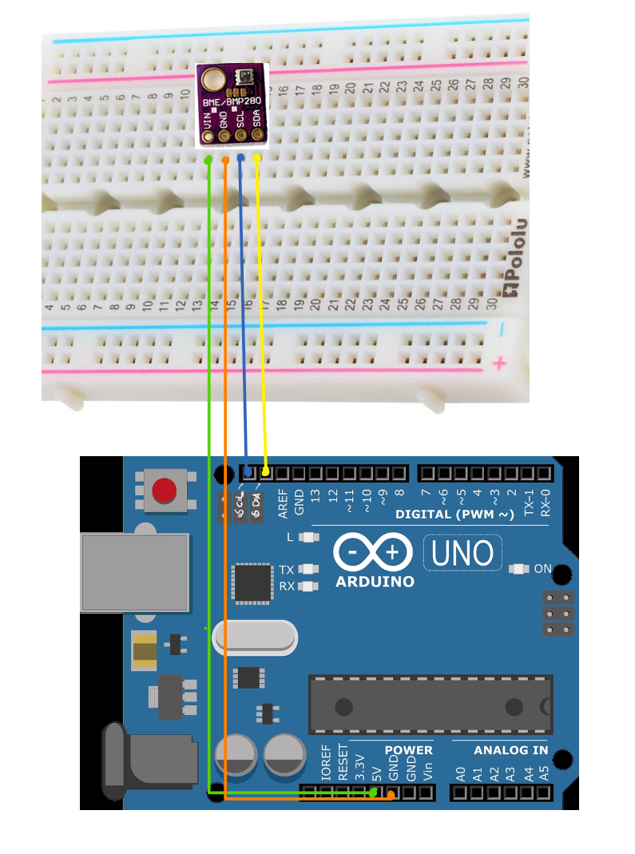
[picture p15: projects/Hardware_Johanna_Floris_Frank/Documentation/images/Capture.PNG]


*Multi-slave single-master set-up for receiving seperate text-based messages and sensor data*
- Using the breadboard: connect Vin and GND (ground) of the BME/BMP280 sensor directly to the 5V and GND pins on the slave Arduino.
- Using the breadboard: connect the  SDA, SCL from the sensor with the slave and further with the master SDA, SCL in one line.
- Ground the slave to the master via the ground next to the SCL/SDA pins
- Open the [master sketch](https://git.science.uu.nl/ued2020/experiment-design-2020/-/blob/master/projects/Hardware_Johanna_Floris_Frank/Arduino_code/Hybrid_Master.ino) and the [slave sketch](https://git.science.uu.nl/ued2020/experiment-design-2020/-/blob/master/projects/Hardware_Johanna_Floris_Frank/Arduino_code/Hybrid_Slave.ino)
- Read the master output, once per loop this should print out the sensor value and a normal value for the temperature.
- If this works, well done. You can now perform your celebration art piece.
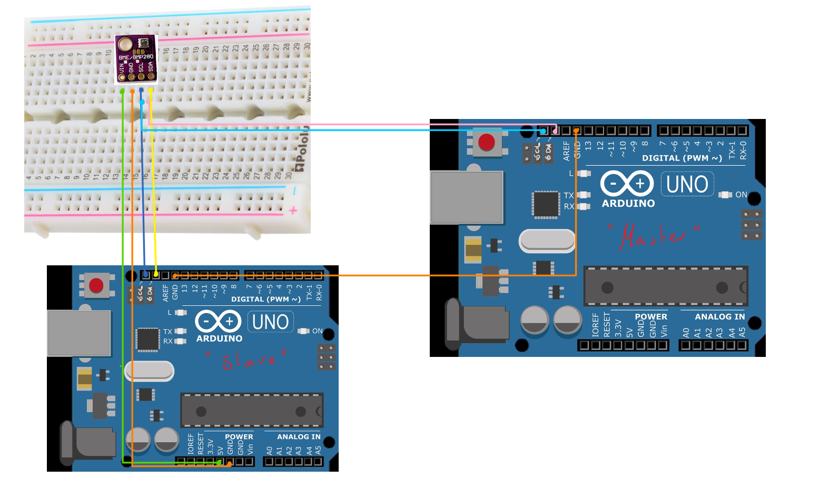
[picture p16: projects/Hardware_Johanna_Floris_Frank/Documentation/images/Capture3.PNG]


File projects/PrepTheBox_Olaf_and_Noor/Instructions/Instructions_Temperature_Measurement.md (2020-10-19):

# Temperature measurement

In this section we discuss a small, quantitative experiment concerning the temperature inside the box we have performed. This test was performed to see whether our design ideas for The Box will lead to properly functioning box. Below we will give the intstructions for this temperature measurement if one would want to repeat this it. 

## Aim of the experiment

The experiment we chose to carry out is one that will test whether The Box needs additional (active) ventilation. We expect that especially the modules and power supply components will generate quite some heat, and we are worried that the heat cannot escape The Box, since it has to be sealed of properly to withstand rainy conditions. By carrying out two measurement-sets (one with The Box completely closed and taped off with dukttape to make it waterproof, and one with two panels opposite to each other slightly shifted down, so that airflow is possible (passive ventilation)). In both measurement-sets, the temperature will be monitored and plotted afterwards. Another important part of the project were the discussions with all other groups to see what their requirements for the box were and to meet all of their wishes. You will also see if the current design of the box meets all of their requirements.

## Safety Measurements and preperations

**Read this section carefully before starting on the experiment!**

During this experiment and in working with the box there are a couple of things you need to pay attention to:

- The edges of the panels of The Box are sharp, do not cut yourself when adding or removing these;
- Some of the panels of the box are attached to it using strong magnets. Be careful with your fingers when working with these plates and magnets.
- The Box is quite heavy. Do not let it run over your feet, for example;
- You will be working with boiling water. Do not burn yourself.
- During the experiment the box will contain boiling water and your laptop. Therefor make sure you do not move the box during the measurements!

Before you start with the experiment it is important that you learn how to assemble and disassemble the panels of the box, and that you understand how you can shift the panels. The panels of the box are attached to the sides and the top using either bolts or strong magnets. To give you a sense of direction: when standing **in front** of the box, the **back panel** and the **right-hand side** are attached using bolts. All other panels are attached using magnets (The top, the front and the left side panel). 

The magnetic side panels (left and front) are held in place by magnets and by in hight adjustable bolts in the beams. These bolts are placed below the panels to make sure the panels are placed at the correct hight. Take some time to try to remove these panels, reattach them and adjust the height of the panels.

The back and the right-hand side panel are attached using bolts. The back panel should be left as is, since its place during the experiment will not change. The height of the right hand side panel will be adjusted during the experiment. This will be done by removing the bolts at the top of the panel and loosening the bolt on the side of the panel. If all bolts are loosend you can shift the panel up and down (during the experiment with passive ventilation the panel will be shifted maximally upwards). Feel free to practice this in advance as well.

## Experimental setup

The experimental setup consists of the following equipment:

- The Box;
- Two glass beakers;
- A water cooker;
- Tools to unscrew the bolts;
- Dukttape;
- An EasyLogger usb (EL-USB-1);

**Installing the EasyLogger**

1. Install the [EasyLogger usb software](https://www.lascarelectronics.com/software/easylog-software/easylog-usb)
2. Plug in the easylogger in a usb port.
3. Click set-up and start USB data logger
4. Set the time measuring interval at 10 seconds and confirm
5. Remove logger from laptop, put the cap on and place inside the box.
6. After the experiment, again plug in the usb logger.
7. click stop the usb data logger and download data.

You can use this software to create the plots or you can use the .txt files.

First make sure you have a working temperature measuremening device and that you have a way of plotting your data.
If you feel comfortable working with the panels of the box, have a working temperature measurement device and all the equipment you can start the experiment following the instruction below. **First read through them beforme starting.**

## Step by step instructions for the experiment

The first thing you need to do is get an idea for the general design of the box. This can be done by reading [this document](https://git.science.uu.nl/ued2020/experiment-design-2020/-/blob/master/projects/PrepTheBox_Olaf_and_Noor/Roadmap-map/Context_and_Theory/BoxReport.docx) and by looking at the sketches provided in [this document](https://git.science.uu.nl/ued2020/experiment-design-2020/-/blob/master/projects/PrepTheBox_Olaf_and_Noor/Roadmap-map/Context_and_Theory/BoxSketch.pdf).

**No ventilation**

During the first measurement the box will be completely sealed off. First, all sides but one are taped off and thus made waterproof. Water is cooked, and put in the two beakers. The beakers are then placed in the box, in the lower compartment (because this one has the steadiest flooring, and we don't want water pouring over the easy logger). Once the initial steam cloud is gone the easy logger is placed inside and the last panel is sealed off. The sensor measures the temperature every 10 seconds. After 25 minutes of measurement the box is opened again and the data is retrieved.

1. Make sure that all panels are placed at the correct height, sealing the box completely.
2. Remove the front panel.
3. Seal of the edges of the panels with dukttape, except for the bottom edges.
4. Start boiling 1.5 liters of water in the watercooker. While this is warming up start do step 5.
5. Place the two beakers on the bottom plate of the box and place EasyLogger on the middle plate of the box. Position of the EasyLogger does not really matter, as long as you make sure it is not directly above the beakers (we do not want it in the middle of the steam coming from the boiling water, as this would make our data unreliable). Make sure everything is stable since the middle plate has holes in it.
6. Once the water has cooked pour 750 mL of water in each beaker and start the temperature measurment.
7. After 30 seconds or so (to let most of the initial steam escape the box) put the front panel in place and seal its edges using the tape.
8. Let the setup stand for **25 minutes**. Do **NOT** move the box during the experiment.
9. While waiting go and talk to other project groups and ask what their requirements are in the functional off-grid measurement station. Consider if the current design of the box meets their requirements or if changes are necesarry. 
10. After the 25 minutes remove the tape from the front panel and remove the front panel itself. Take the Easylogger out of the box, stop the measurement and process the data.
11. Take out the beakers with water (**Caution, the beakers with water can still be very warm**)

**Passive Ventilation**

The second measurement has two opposite panels of The Box slightly ajar (The left and the right panel), and thus has a passive ventilation channel.

12. Remove the tape from the left and right hand side panels
13. Lower the **left** panel untill there is a gap of around 20 centimeters at the top of the panel. The panel can be lowered by clicking the magnets on the panel on the lower ones than their original counterparts on the frame of the box.
14. Raise the right panel maximally. There will be a gap of around 15 centimeters at the bottom. You can raise the panel by screwing it loose and placing it on bolts that stick out. Tape it extra tightly to keep it in place.
15. Seal the edges of the side panels.
16. Repeat step **4** up untill step **11**

Below, a few images can be seen. The first one shows the completely sealed off Box, the second one shows the passive ventilation setup, and the third one shows the insides of The Box. These can give some indication of what the set-up looks like. Note that we did not use the EasyLogger when carrying out the experiment, but rather the entire Arduino setup from the temperature control group. This is why we have enclosed our laptop in the box as well, this can be seen in the second picture.

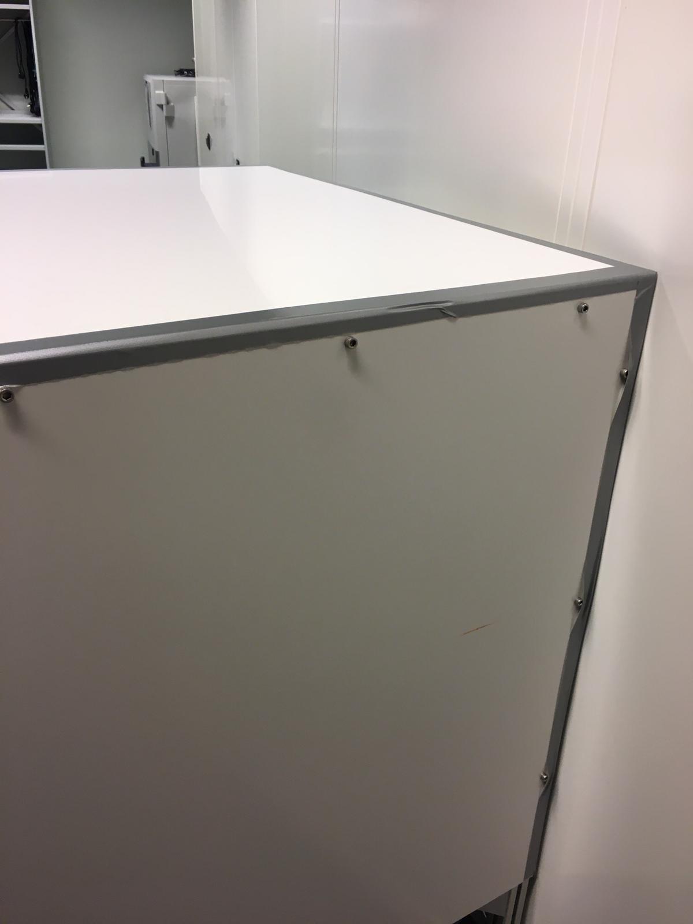
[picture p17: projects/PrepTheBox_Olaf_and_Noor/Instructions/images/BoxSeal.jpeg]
The sealed off Box


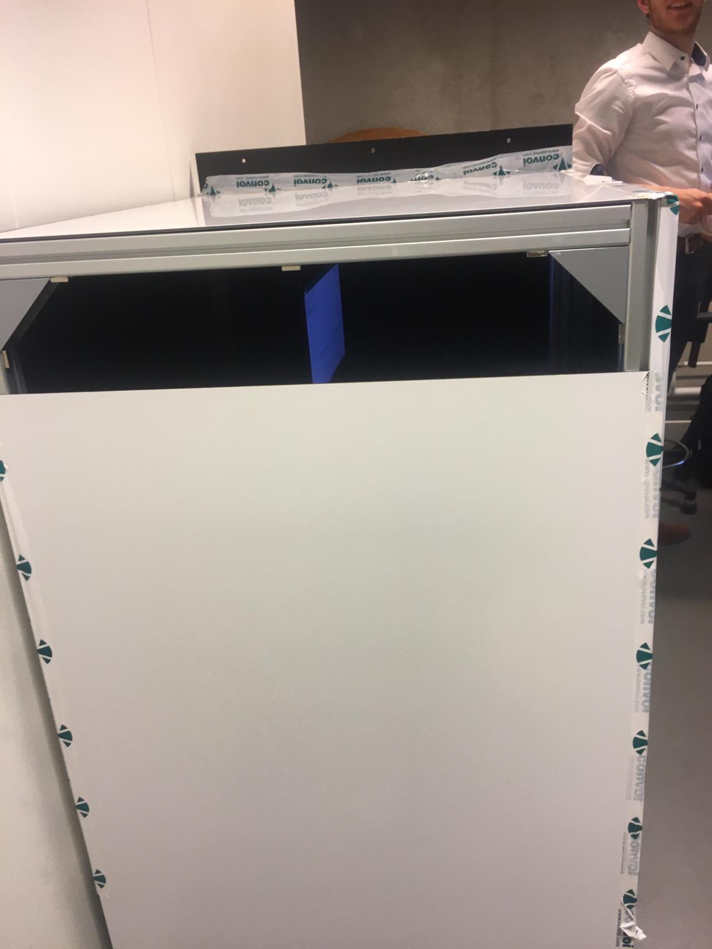
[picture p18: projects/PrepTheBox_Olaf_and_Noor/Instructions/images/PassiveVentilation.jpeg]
The passive ventilation setup


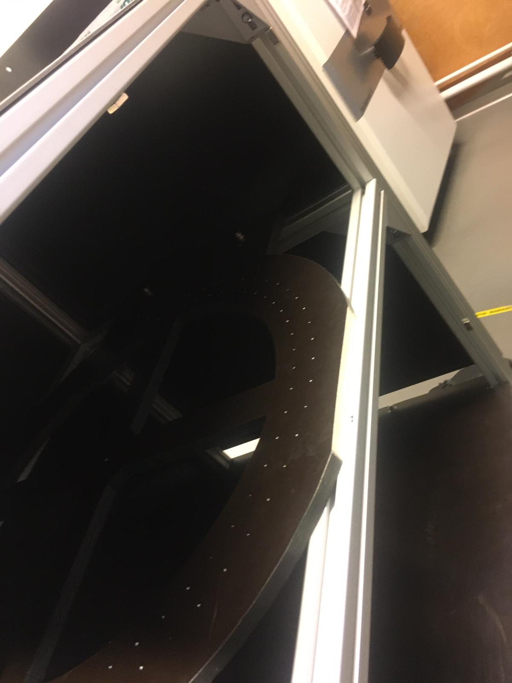
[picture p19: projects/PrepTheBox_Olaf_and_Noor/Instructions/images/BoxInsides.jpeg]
The insides of the Box™


## Results

Create a plot of the results. Below the results of our experiment can be seen. What can you conclude based on your measurement? Also, does the design of the box meet the requirements of the other sub-project groups? What would you have done differently?

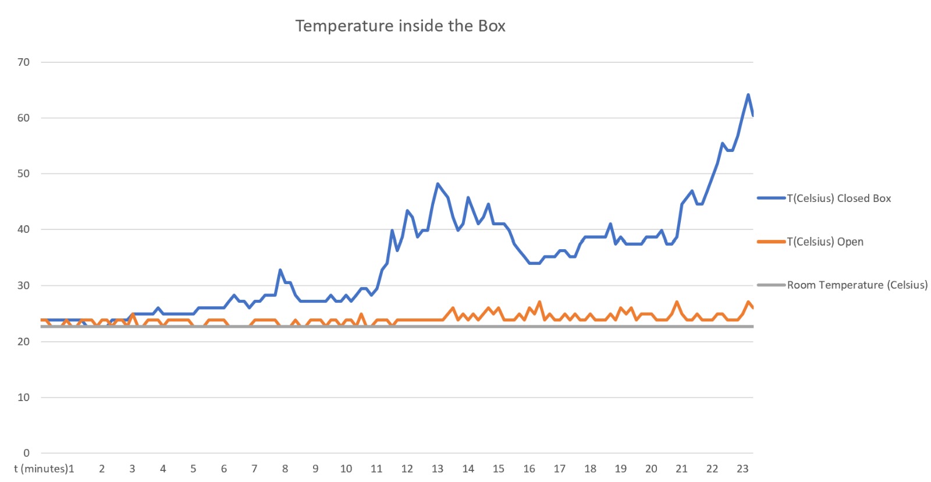
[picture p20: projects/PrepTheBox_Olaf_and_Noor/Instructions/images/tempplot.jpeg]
tempplot


## Feedback form

Please provide feedback on our project. You can use [this template](https://git.science.uu.nl/ued2020/experiment-design-2020/-/blob/master/Coordination/_Templates/peer_evaluation.md) to provide feedback and post it into the [feedback folder](https://git.science.uu.nl/ued2020/experiment-design-2020/-/tree/master/projects/PrepTheBox_Olaf_and_Noor/feedback). 

The best of luck with reproducing our experiment!

Cheers,

Noor and Olaf

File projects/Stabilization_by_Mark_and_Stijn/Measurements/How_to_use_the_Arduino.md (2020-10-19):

Because our feedback group apperently had never worked with an arduino before, we decided that we would write a small little manual on how to operate arduino.

To start, one should read the following internet page, where is explained what arduino is, how to use it and etc [Click here](https://www.arduino.cc/en/Guide). From this page, one can also download the arduino-software. 

Once you have donwloaded this software, you should also download the needed accelerometer-code [Click here](https://github.com/jrowberg/i2cdevlib). Once downloaded, you should look for your specific accelerometer in the arduino-folder (If you would have a accelerometer that doesn't work with arduino, you can also find code for those over here). In our case, we used the MPU6050. Once you found your accelerometer, you copy this entire folder in your "arduino-libraries"-folder, along with the I2Cdev (which is needed for the arduino to be able to find your accelerometer). In most cases, this "arduino-libraries"-folder can be found at "C:\Program Files (x86)\Arduino\libraries". However, this depends on where you saved your arduino-software, so you try to find this yourselves. 

Once you have done this, open your arduino-software. Once opened, click on the following: Files -> Examples -> MPU6050 -> MPU6050_DMP6. In this file, all the code that we used can be found. With this code, you are able to measure the yaw, pitch, role and accelerations in x,y and z.

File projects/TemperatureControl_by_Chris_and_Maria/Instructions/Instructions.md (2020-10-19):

In this project you have to make a circuit which will measure the temperature of the box and using a peltier control it in a range you can define. Here are the steps you need to follow in order to achieve this:

### Part 1: Downloading and Installing Arduino

Go to [this site](https://www.arduino.cc/en/Main/software) and choose which suits for you depending on your operating system [here](Downloading_Arduino.jpg)

Then you can easily install the program.

Open the Arduino, Go to tools -> Board “Arduino Yun” -> Arduino Uno

Now you are ready to copy-paste the [code](../documantation/data/code.txt)!

### Part 2: Making the circuit

First, notice that you have all the required items:

1 Arduino Uno

1 BreadBoard

1 sensor PTA 100

150 Ohm Resistor

4 Mosfets

1 Peltier with 1 heatsink 

[The box](the_box.jpg) (the arrow shows where you can put the peltier)

Extra [Power Supply](power_supply.jpg)

Couple of Wires

During this part it will really help you to have open the [schematic](https://git.science.uu.nl/ued2020/experiment-design-2020/-/blob/master/projects/TemperatureControl_by_Chris_and_Maria/documantation/data/schematic.pdf). 
We can devide this part into 2 subparts:

1. Sensor subpart

Connect the PIN Ground of Arduino with the BreadBoard. 
The 150 Ohm Resistor must be connected with the ground and with the sensor.
The sensor has to be also connected with the PIN Ao and at 3.3V of Arduino.
[This](Sensor_Part.jpg) picture may help you.

2. Cooling/ Heating subpart

[This](Mosfet.png) picture will help you to understand when you see a MOSFET which side is the source, gate and drain.

**Mosfet 1**

Gate connected with:

- PIN 10 of Arduino

- Gate of Mosfet 3

Drain connected with 

- Gate of Mosfet 2

Source connected with 

- One side of Peltier(1)

- Drain of Mosfet 4

**Mosfet 2**

Source  connected with

- Other side of Peltier(2)

- Drain of Mosfet 3

Gate  connected with

- Gate of Mosfet 4

**Mosfet 3**

Source connected with

- Ground

**Mosfet 4**

Gate connected with

- PIN 2 of Arduino

Source connected with

- Ground

Also you will connect the Power Supply with the drain of Mosfet 2 and Mosfet 3  and you will turn it on to 12V.

[This](CoolingHeating.jpg) picture will help you have a better understanding of the above part.

### Part 3: Connecting the code with the arduino

Connect the computer with the Arduino using a wire.
Open the program at your computer with the code and press upload.
It is ready!
If you want to see the value of Temperature just go to Tools and press Serial Monitor!
Also you can easily change the values of the range in the Temperature in this part of the code:
int T_L =15;
int T_H= 30;

Good luck :)

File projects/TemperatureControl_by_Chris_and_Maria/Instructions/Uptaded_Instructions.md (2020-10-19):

In this project you have to make a circuit which will measure the temperature of the box and using a peltier control it in a range you can define. Here are the steps you need to follow in order to achieve this.

Notice: Don't expect the heating/cooling part to function normally yet. However, once you have completed the setup, the values of the temperature should be displayed on your screens. So, the aim until now is to reproduce the complete setup and to measure the temperature.

**Safety Instructions**: 

Although we are in a range of low voltage that it is not farmfull, attention must be taken when you are controlling the voltage of Power Supply. What we mean is be carefull to set it in the value we have indicated and not much more. If you do that there is nothing to worry about!

As you will see below, we use Peltier- an item that from its one side will be heated and on the other side cooled. (This is explained from the direction of the current, if you want to learn more about its operation see [context and theory](https://git.science.uu.nl/ued2020/experiment-design-2020/-/blob/master/projects/TemperatureControl_by_Chris_and_Maria/documantation/data/template_Article.pdf)). So, when it is activated it can be very hot so we strongly advise you to not touch it in that case!!!

### Part 1: Downloading and Installing Arduino

Go to [this site](https://www.arduino.cc/en/Main/software) and choose which suits for you depending on your operating system [here](https://git.science.uu.nl/ued2020/experiment-design-2020/-/blob/master/projects/TemperatureControl_by_Chris_and_Maria/Instructions/Downloading_Arduino.jpg)

Then you can easily install the program.

Open the Arduino, Go to tools -> Board “Arduino Yun” -> Arduino Uno

Now you are ready to copy-paste the [code] (will be added)!

Notice: It is necessary to have Arduino Uno which provides us with 5V, in contrast to Arduino Due which can provides us only with 3.3V. So don't try to do this with Arduino Due!

### Part 2: Making the circuit

First, notice that you have all the required items:

1 Arduino Uno

1 BreadBoard

1 sensor PTA 100

150 Ohm Resistor

4 Mosfets

1 Peltier with 1 heatsink 

[The box](https://git.science.uu.nl/ued2020/experiment-design-2020/-/blob/master/projects/TemperatureControl_by_Chris_and_Maria/Instructions/the_box.jpg) (the arrow shows where you can put the peltier)

Extra [Power Supply](https://git.science.uu.nl/ued2020/experiment-design-2020/-/blob/master/projects/TemperatureControl_by_Chris_and_Maria/Instructions/power_supply.jpg)

Couple of Wires

During this part it will really help you to have open the [schematic](https://git.science.uu.nl/ued2020/experiment-design-2020/-/blob/master/projects/TemperatureControl_by_Chris_and_Maria/documantation/data/schematic.pdf). 
We can devide this part into 2 subparts:

1. Sensor subpart

Connect the PIN Ground of Arduino with the BreadBoard. 
The 150 Ohm Resistor must be connected with the ground and with the sensor.
The sensor has to be also connected with the PIN Ao and at 3.3V of Arduino.
[This](https://git.science.uu.nl/m.lekou/experiment-design-2020/-/blob/master/projects/TemperatureControl_by_Chris_and_Maria/Instructions/Sensor_Part.jpg) picture may help you.

2. Cooling/ Heating subpart

[This](https://git.science.uu.nl/ued2020/experiment-design-2020/-/blob/master/projects/TemperatureControl_by_Chris_and_Maria/Instructions/Sensor_Part.jpg) picture will help you to understand when you see a MOSFET which side is the source, gate and drain.

Notice: The naming of the below Mosfets is just indicating, namely you will choose randomly which Mosfet will be the 1st. 2nd etc. 

**Mosfet 1**

Gate connected with:

- PIN 10 of Arduino

- Gate of Mosfet 3

Drain connected with 

- Gate of Mosfet 2

Source connected with 

- One side of Peltier(1)

- Drain of Mosfet 4

**Mosfet 2**

Source  connected with

- Other side of Peltier(2)

- Drain of Mosfet 3

Gate  connected with

- Gate of Mosfet 4

**Mosfet 3**

Source connected with

- Ground

**Mosfet 4**

Gate connected with

- PIN 2 of Arduino

Source connected with

- Ground

Also you will connect the Power Supply with the drain of Mosfet 2 and Mosfet 3  and you will turn it on to 12V.

[This](https://git.science.uu.nl/ued2020/experiment-design-2020/-/blob/master/projects/TemperatureControl_by_Chris_and_Maria/Instructions/CoolingHeating.jpg) picture will help you have a better understanding of the above part.

### Part 3: Connecting the code with the arduino

Connect the computer with the Arduino using a wire.
Open the program at your computer with the code and press upload.
It is ready!
If you want to see the value of Temperature just go to Tools and press Serial Monitor!
Also you can easily change the values of the range in the Temperature in this part of the code:
int T_L =15;
int T_H= 30;

Good luck :)

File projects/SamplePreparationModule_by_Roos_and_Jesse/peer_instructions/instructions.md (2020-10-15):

## Instructions:
Before you can use the box, you have to attach the retractable pipe to the pvc pipe.
This attaches by friction so you can just slide the retractable pipe over the pvc pipe.
After this, you have to attach the black wire to the - and the yellow wire to the + of the 12V battery from the power group.
Now the box is ready for use!

You can find the description of the testing in [this](https://git.science.uu.nl/ued2020/experiment-design-2020/-/tree/master/projects/SamplePreparationModule_by_Roos_and_Jesse/Testing) directory.
For borrowing the anemometers you should contact Pascal Koopman (p.koopman@uu.nl).
For repeating the chemical resistance test you should contact Jesper Moes (j.r.moes@uu.nl) from CMI, or reach out to someone else with access to the lab. Feel free to also do additional tests. These were the chemicals we had readily available and we thought would be nice to test since they are the typical solvents that are used along with some common acids. 

### Safety Instructions
When testing the chemical resistance of the coated wood, you should wear a lab coat and safety goggles. For some actions you may have to wear acid resistant gloves. The lab supervisor will tell you when you need to wear gloves. A lab coat and safety goggles can be borrowed from the lab. As also mentioned in the coating_testing file, you should always add water to your beaker first and then the acid.

When using chemicals you should look up the msds safety sheets of each chemical. Because you are working in small quantities, the safety instructions come down to washing your skin under cold running water for 10 minutes in case of a spill. When chemicals come into contact with your eye you should wash your eyes with water as well.
In the scenario where you spill acid elsewhere try to remove as much as possible by pipetting it up, if only a bit of acid is left you can dilute it with water and wipe it up with paper.
Make sure to wash your hands after performing any testing since trace amounts of chemicals may be left on your hands. 

When using the 12V battery there is a small risk of the battery exploding when short-circuiting it. Carefully attaching the wires as described above will not allow you to short-circuit it.

#### Aqua Regia
Aqua Regia (King's Water) is an acid which is famous for being able to dissolve nobel metals such as gold and platinum, hence the regia in its name. It consists of a 3:1 molar ratio of hydrochloric: nitric acid and is yellow of color. You should ask one of the lab supervisors to make it for you. We asked Naud van Bunningen (a.j.vanbunningen@uu.nl) to help us prepare it.

### Finn Pipet
In this section we will give a small instruction on how to use a Finn pipet. There are different models of Finn pipets that enable you to pipet different quantities of liquids. The pipet that you will need can pipet a volume of 1-5ml. The quantity can be changed by turning the knob at the end. For some pipets you need to pull this back before you are able to turn it. Add a plastic tip to the pipet when you want to start pipetting. When you push the knob you will encounter two 'stops', try it a couple times to see if you feel it. When you want to suck up liquid you push until you reach the first stop. During the entire pipetting process you should keep your pipet vertical. Now place your pipet point in the liquid and slowly release the knob to suck up the liquid. To squirt out the liquid again push until the second stop while keeping the pipet point against your glass at an angle of approximately 40°. When pipetting a volume for the first time, follow this procedure in the beaker containing the liquid you wish to pipet, before you pipet it to another beaker. This is because there is always some residual liquid in the pipet tip after pipeting. This also means that you have to keep your pipet tip pointing downwards. Work up in increasing volumes, to keep the pipetting as accurately as possible. When you are done pipetting a specific substance you can dispose the tip by pressing the ejector button next to the knob. 

If you think this explanation is too complicated and would rather see an [instructional video](https://www.youtube.com/watch?v=QGX490kuKjg) feel free to watch it. This might also help visualising the process.

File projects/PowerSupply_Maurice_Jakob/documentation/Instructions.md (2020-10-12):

# Instructions

## purpose and theory
### Goal of the project

The goal of the power supply project is to construct a circuit that supplies stable power to all electronic devices (loads) of the science station in an off-grid fashion.
For that we chose power generation by solar panels, which makes us independet of wall outlets.
As the power coming from the panels is dependent on lighting, we need to interconnect a power storage that can supply stable power when charged up.
The loads of the science station can in principle run on DC or AC current and at different voltages. This affects the choice of batteries and additional components we need as described below.

### A comparison of different strategies

In the scope of electronics, there are a thousand different ways to construct what you want, with additional options left and right.
We narrowed it down to three different categories.
The two extremes are ready-made solutions and a full DIY plan of building the setup.
In between is the use ready-made parts that fullfill certain sub-tasks with some hand-made solutions and connections.
Here I will go over the general advantages and disadvantages of each and why we made certain choices.
A full list with examples of parts can be found [here](Comparison_powerbank_DIY.md).

Ready-made solutions are easily available for small scale projects.
Think of powerbanks with a solar panel attached that can be put on a backpack.
These are intended to charge a phone or laptop while on a hike for instance.
The major advantage is that its a very simple solution, it provides a 5V USB output that is used by many small-scale devices and some of the more advanced powerbanks ever have 230V AC output.
A disadvantage is that they are not modular at all, you get what you buy with very limited or no options to modify to your needs.
In order to get more options, very expesive systems are required and even then are limited to 50W output power most of the time.
The solar panels on these setups are very small and cause the time to charge the powerbank to increase to inconvenient amounts.

A full DIY would consist of the hand-made construction of each of the electronic component, made from basic parts like resistors, capacitors, transistors and opamps.
The obvious advantage is the full control of the setup is gives.
Any voltage or current can be obtained by tuning the elements to your liking and expanding the setup in the future usually has no limitations.
On first thought, the goal of this projects does not sounds all that complicated.
However, batteries require more than just a voltage to charge themselves.
A lead-acid battery, for instance, has [3 stages](https://batteryuniversity.com/learn/article/charging_the_lead_acid_battery), a constant current, a constant voltage and a topping stage.
To regulate this, a complicated feedback loop and voltage/current generation circuit is required.
This must include properties of the battery used hardwired into the circuit.
Other [DC/DC and DC/AC converters](https://learn.libre.solar/development/dcdc_converter.html#linear-regulators) are relatively simple in concept, but may require specials parts that can operate at higher power outputs that are not easily obtained.
Safety and the shielding of these components requires a  lot of practical knowledge of electronics.
Hence, all-in-all such a setup is very versatile, cheap and modular. But on the other end, it requires up to 100 hand-picked parts tuned to exactly the right values which need to be calculated first.

A third option is the use of some ready-made parts for complicated task, combined with hand-made parts where possible.
This solution attempts to find a middle ground between the required knowledge, expertise and the cost of the setup, while still obtaining the option for all reasonable output voltages and power supplies.
An example is a solar charge controller, which consist of a DC/DC converter that turns the voltage from a solar panel into the correct one for charging a lead-acid battery.
Additionally, this provides the charging scheme for such a battery, with deep-discharge and overcharge protection.
The output would be the regular voltage of the battery in question.
This voltage (approximately 12V) can be used directly for scientific devices and downconverted to another standard, the 5V for small USB devices.
A powerbank can be used as intermediate 5V power storage for more convenient use.
An inverter can be used to obtain 230V AC power, which devices that are meant for indoor use need.
Overall, this results in the modularity that is comparable to a full DIY setup, but is still constructable in an afternoon given the parts and some tools.
The power output can reach high values that are not obtainable from ready-made solutions.
Regarding the cost, it is considerably lower than a ready-made solution with similar properties.
With spending some extra time on looking up the right parts, it is usually a bit more than individual basic parts, but it is not uncommon to find mass-produced devices that are very cheap in comparison. Hence, we chose the latter option with how we want to build our project.

### Project outline

The central unit of this setup will be the batteries that store and supply the science station.
In order to supply voltages that are widely used, a 12V lead-acid battery and a 5V litium-ion USB-powerbank are combined.
The 5V USB connection are the most convenient and widely used for small electronics like arduinos, which are the main controllers for the science stations.
Some other devices might need a higher voltage or even an alternating current.
This is easier to achieve with a 12V lead-acid battery, as it can suffice a higher output power.

The next step is a way to charge both the batteries independently off the grid.
A solar panel can supply power anywhere it is, even some at cloudy days.
Each battery has its own pattern of charging.
Luckily, 12V lead-acid batteries are commonly combined with solar panels as off-grid or self-sustaining setups.
Therefore a solar charge controller is an easy tool to convert the variable output voltage of the solar panel into a useful one for the battery.
It also has deep-discharge and overcharging protection features, which come in handy. 
This charge controller provides a connection for the loads as well, as a 12V DC output.

With a DC/DC converter, this is converted into a 5V supply, that can charge the Lithium-ion battery as well.
A lead-acid battery is also used in cars and we used a tool for cars that can convert it to 230V AC power as additional power supply for devices that need regular wall-socket power.

To communicate with the rest of the science station, a connection with an arduino can be made.
This monitors the capacitance of the batteries and can shut down the experiment when the batteries are running out of power.
A load switch can disconnect the load, to avoid deep-discharging the batteries.
In our case, both the Charge Controller and the powerbank have internal load-switches that take care of this already.
However, additional protection and control can be obtained by adding these.

Below, A schemetic can be found of the setup.

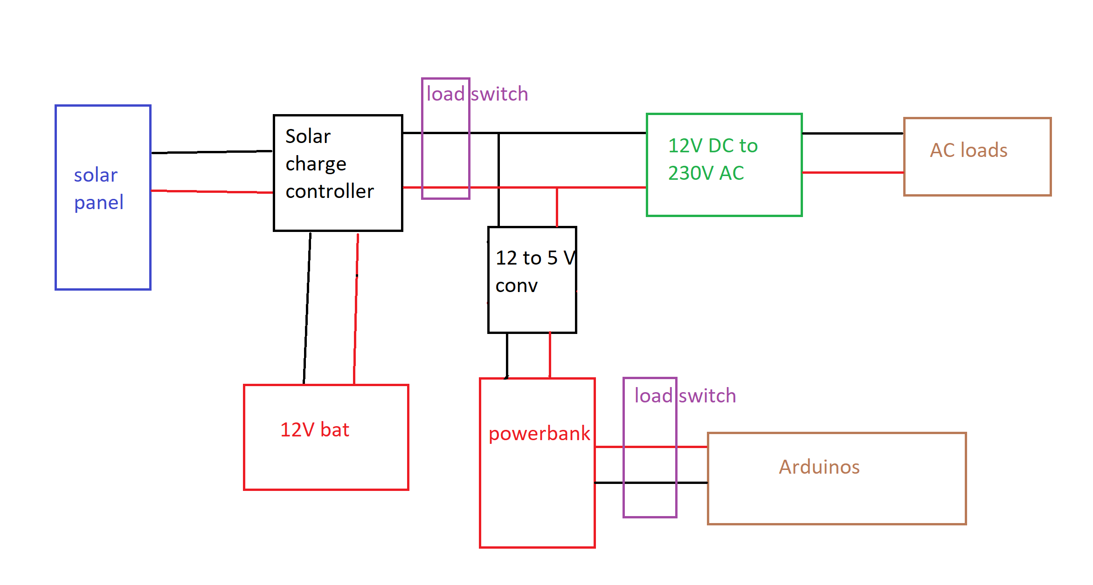
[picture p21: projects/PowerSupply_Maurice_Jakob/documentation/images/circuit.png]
Circuit of project


### Important considerations

The lead battery has to be charged with a voltage close to its nominal voltage of 12V. 
Also it is sensitive to overcharging or deep discharge. 
This is taken care of by the charge controller, which also internally downconverts the input voltage from the solar panel.

As the charge controller will shut everything down in case of too high or low battery voltage and that can be troubling for some components there is a need for additional voltage monitoring.
This enables the user to disconnect the loads in time.

As described above, the lead battery is the most sensitive component of the setup.
It is needed because of AC loads in the science station.
The current from the solar pannel is DC and most loads use 5V DC which can be supplied via USB, which makes a power bank the convenient option.
However, an inverter that makes AC current out of DC input cannot connect to a power bank so the 12V lead battery is needed.

### Possible sources of noise

Not a source of noise but a nuisance is the weather dependent power supply of the solar panel
Other things: inverter uses standby power, the voltage measurement for the load switch is kind of inaccurate because of use of a high-resistance voltage divider.
Each of the DC sources will have a few percent variance. However, this is not an issue, since the tolerance of the devices used is fairly large.

## safety recommendations
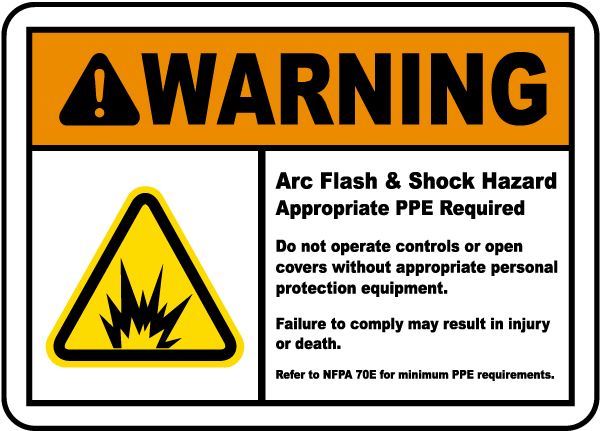
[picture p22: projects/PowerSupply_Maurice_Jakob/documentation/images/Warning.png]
Warning


Do not ever short circuit the 12V lead-acid battery, it will explode!

In order to safeguard yourself and the setup, be very careful with where you leave the cables laying around.

Only remove the safety caps from the poles of the battery when attaching the cable.
Still be careful where the other end of the cable is.
immediately put the safety caps back on once you remove the cable. 

## assembly + test measurements

### Step 1: Set up Charge controller
1. Put the Charge controller (CC) in an upright position (see picture)

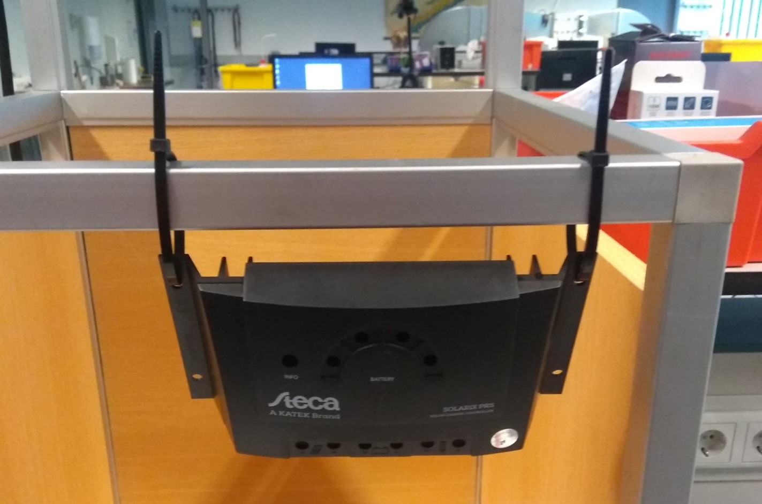
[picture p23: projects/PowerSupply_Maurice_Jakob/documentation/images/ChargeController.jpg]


2. Connect the battery to the CC by first connecting the red cable (containing a fuse) to the positive pole of the CC, then the black to the negative.
Images on the CC indicate which 2 connections are for the battery (eg. the the in the middle).
3. In the same order, connect the solar panel to the CC.
Use the solar cable with MC4 connectors attached to one side.
Those determine where to attach it at the panel.

**Measurement** \
Measure the voltage between the poles of the battery the battery using a multimeter over at least 10 minutes. \
Check if it is increasing in the range 12.0-13.8 V.
This means it is charging.
Compare that with the charging curve in the battery [datasheet](https://asset.conrad.com/media10/add/160267/c1/-/en/000250916DS01/datablad-250916-conrad-energy-12-v-12-ah-loodaccu-12-v-12-ah-loodvlies-agm-b-x-h-x-d-151-x-95-x-98-mm-kabelschoen-635-mm-onderhouds.pdf) 
Measure the open-circuit voltage of the solar panel.
For that, temporarily disattach the cables from the CC and connect them with the multimeter.

### Step 2: Connect loads
In the setup there are two loads, the inverter and DC/DC converter.
Those have to be connected to the same poles of the CC.
1. Twist the cable ends with matching colours together
2. Connect them to the CC, positive pole first.
3. Connect the open end of the modified USB cable to the output poles of the converter.
4. Connect the power bank. 

**Measurement** \
Interconnect the multimeter between converter and powerbank to measure the current. \
Check the specifications of powerbank and converter regarding maximum input/output current. \
Measure the current on the input poles of the converter with no load attached. 
This is the stand-by current of the DC/DC converter.

### Optional Step 3: using the arduino to measure the battery voltage
Specific instructions on how to use the arduino can be found [here](./Arduino/Arduino_Instructions.md).
This is still a work in progress and does not provide much use for now.
Therefore, there are no nice connection at the moment.
However, banana plugs and alligator clips can suffice.
The goal is to use this to keep an eye on the battery capacity and send a message to the rest of the seup once the battery runs low.

## Results

| Quantitiy | Result |
| --- | --- |
| battery voltage |  12.0-13.8 V |
| solar panel open-circuit voltage| depends on irradiation | 
| powerbank current | (1.01 +- 0.01) A |
| stand-by current DC/DC | (0.05 +- 0.01) A |
| R1 | 19.902 kOhm |
| R2 | 4.717 kOhm |

## outlook (what can be improved)

The voltage measurement using the Arduino can be expanded.
By choosing a minimal and maximal voltage value informed by the discharge characteristic of the [datasheet](https://asset.conrad.com/media10/add/160267/c1/-/en/000250916DS01/datablad-250916-conrad-energy-12-v-12-ah-loodaccu-12-v-12-ah-loodvlies-agm-b-x-h-x-d-151-x-95-x-98-mm-kabelschoen-635-mm-onderhouds.pdf) one can infer wether the battery is over– or discharged or malfunctioning in another manner.
This can then either be displayed in the science station software GUI and dealt with by the user by manually switching off the loads or an automatic load switch can be implemented.
Swtiches in general would improve the flexibility of the power supply.
They would enable (dis–)connecting any desired device in the circuit without the need of (un)screwing connections.
This would greatly improve overall usage of the system within the science station.

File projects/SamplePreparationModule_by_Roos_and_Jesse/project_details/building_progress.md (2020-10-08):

### Sunday 27-09:

We went to the Praxis to buy the wood that is needed for the sample preperation model. 
We bought two 61x120cm pieces of 'multiplex' that has a thickness of 1.2cm.
It was cut for us in 2 pieces of 50x50cm, two pieces of 50x27.6cm and one piece of 50x30cm at Praxis.
We also bought a wooden slat and a plastic rail in which the plexiglass can slide. (insert picture)
Also a piece of pvc pipe with a diameter of 100mm and a retractable pipe with a diameter of 100mm were bought.
At home the pieces of wood were painted on 1 side with a mat white wood paint.
The plastic rail was glued to the wooden slat with construction glue and cut up in 2 pieces of 27.6mm with a hand saw.

### Monday 28-09:

We went to the workshop in the Bleeker building to drill and screw the wood together.
First holes that were the same size as the major diameter of the screw were drilled in one of the boards.
These holes were countersinked on both sides to ensure a tight fit.
In the board that will be attached to the first board, first a approximately 2mm deep hole was drilled with the same size as the screw.
Then a hole with the size of the minor diameter of the screw were drilled as deep as the screw would go.
After drilling all the holes, the boards was screwed together with a normal screwdriver.
We also got a computer fan from Dante which we will have to attach later.

### Thursday 01-10:

We bought a polyurethane coating on wednesday and wanted to coat the workspace with it today. Additionally we decided that we wanted to coat another piece of wood with the polyurethane coating. This extra piece of wood can be used to test the chemical resistance after everything is dry. This is just to keep the module pretty, no other reason. When we arrived at the Minnaert building we found out that Dante had provided us with plexiglass as well. We used kit to install the rail which hold the sliding plexiglass. Unfortunately the plexiglass was just a bit bigger than we had hoped. Making the sliding pretty difficult. We now have a friction fit meaning that we don't need to drill any holes in you rail system. We only had time for one layer of coating today since the polyurethane needs to dry for approximately 2 hours.

### Friday 02-10:

The plan for today was to see if we could get the fan working. After have discussed with the power group we decided it might be best to have a USB male which can be plugged in. We brought an old wire and a powerbank to test if the fan works. After stripping the old wire we attached the Black-> Black and the Red -> Yellow in the 4-pin. Plugging the USB male into the powerbank did indeed make it turn meaning that we now have a working fan, which only needs to be installed. Additionally we also managed to cover the workspace with a second layer of polyurethane.

### Monday 05-10:

We came in with the plan to finish most of the construction work. We made an appointment with Dante to get our final piece of plexiglass, and we made an appointment with Otto to drill some additional holes, in order to attach the plexiglass, and to cut out two holes in the top of the module. The top of the module now has both a window and a ventilation outlet. The reason we added a window in the top of our module is to make the module easier to work with. Since the module is quite deep and not so high it was sometimes inconvenient to work in the module. If the module was on a relatively low working bench you would have to squat while working in it. The addition of the window in the top of the box was a way to circumvent this problem. We also hooked up the fan to a 12V power source and this significantly increased the power of the fan. According to the powergroup this gives no problems for them since they have a 12V battery. We also attached the fan to the inside of the box where it is now suspended from the 'ceiling'. Currently, one of the holders, with which we attached it to the ceiling, prevents the fan from turning so we have to fix this when we are going back to the lab to do experiments. The pvc pipe we bought was cut down a bit by Otto and a hole was drilled in the side through wich the wires can go. The pvc was glued to the top with construction glue.

### Wednesday 07-10

Today we tested the windspeed generated by the fan using an anemometer and we tested the chemical resistance of the coated wood. The windspeed was measured by holding an anemometer in certain positions in and around the box. More information can be read in [this](https://git.science.uu.nl/ued2020/experiment-design-2020/-/blob/master/projects/SamplePreparationModule_by_Roos_and_Jesse/Testing/testing_airflow.md) file. We also taped the sides of the box after measuring. Today we also went to the CMI lab to test different concentrations of acids and solvents on the coated wood. This was guided by Jesper. And information about this process can be found in [this](https://git.science.uu.nl/ued2020/experiment-design-2020/-/blob/master/projects/SamplePreparationModule_by_Roos_and_Jesse/Testing/testing_coating.md) file. After 24 hours a feel test will be done to fully determine the effects of the liquids. 

### Thursday 08-10

Today a feel test of the coating was done. This was to see if any of the chemicals had an effect on the coating that was not visible. Results can be found in the [coating testing](https://git.science.uu.nl/ued2020/experiment-design-2020/-/blob/master/projects/SamplePreparationModule_by_Roos_and_Jesse/Testing/testing_coating.md).

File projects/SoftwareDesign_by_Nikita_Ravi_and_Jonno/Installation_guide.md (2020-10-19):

The following steps will guide you how to get everything running from scratch (reading [Possible problems](#Possible problems) section recommended).

### Windows installation

**1. Go to https://github.com/SanliFaez/labphew**

   1. Download the zip archive after pressing the "Code" button
   2. Extract the zip into a place of your choosing

   Another variant how you can get the copy of this repo:
   1.  Open the command prompt. You can open the command prompt by searching "powershell" or "cmd" in windows search. Or type Win+R, type "powershell" or "cmd" and press Enter
   2.  Type **git clone https://github.com/SanliFaez/labphew** . This command will make a copy of this repo in your current folder without need to zip/unzip the repo. You need to have Git installed on your system

**2. Go to https://git.science.uu.nl/ued2020/experiment-design-2020**

   1. Download a zip of the repository. Extract the zip. Or you can do the same via Git as with labphew in the previous step
   2. In your local files, go to experiment-design-2020/projects/SoftwareDesign_by_Nikita_Ravi_and_Jonno/Programs
   3. Find the file analog_discovery_2_model.py. You will need it in the following step.

**3. Install anaconda from: https://www.anaconda.com/products/individual**

   1. Open the anaconda prompt by searching "anaconda prompt" in windows
   2. Navigate to your copied repository folder "master-labphew" in the anaconda prompt using ***cd C:/path/to/dir/.../master-labphew*** (you can go up a folder using **cd ..**). Or just copy the path from file explorer and type **cd** and then insert the path
   3. Now when you are in the labphew project folder go to subfolder /labphew/model and find file analog_discovery_2_model.py. Yeah, it has the same name as the file in experiment design repository. And now replace this file in labphew repository with the file we asked you to remember in step 2.3. When done, return back to labphew project folder.
   4. Type "***pip install -e .***" (make sure to include the dot at the end) and press Enter
   5. (Do only if use Spyder IDE) Type ***pip install pyqtwebengine*** and press enter *twice* (the second time after the first one is done). This package is needed only for Spyder IDE, without it it won't start
   6. Type ***pip install pyqtgraph*** and press enter

   **Or** you can do all the same but without installing heavy and slow anaconda. The main benefit which anaconda gives is that it installs Python to your computer. But if you already have Python installed, you probably want to go without anaconda.

   1. Navigate to your copied repository folder "master-labphew" in the command prompt (watch 1 step) using ***cd C:/path/to/dir/.../master-labphew*** (you can go up a folder using **cd ..**). Or just copy the path from file explorer and type **cd** and then insert the path
   2. Now when you are in the labphew project folder go to subfolder /labphew/model and find file analog_discovery_2_model.py. Yeah, it has the same name as the file in experiment design repository. And now replace this file in labphew repository with the file we asked you to remember in step 2.3. When done, return back to labphew project folder.
   3. Type ***pip install -e .*** and press Enter (if you had already installed it, be sure to uninstall and reinstall with the new file. We recommend to do the install from scratch however)
   4. (Do only if use Spyder IDE) Type ***pip install pyqtwebengine*** and press enter *twice* (the second time after the first one is done). This package is needed only for Spyder IDE, without it it won't start

**4. Download and install Waveforms program from: https://mautic.digilentinc.com/asset/110:waveforms-windows-64-bit-download. Agree to default options. The detailed guide(on Windows you don't need it) is [there](https://reference.digilentinc.com/learn/instrumentation/tutorials/analog-discovery-2-getting-started)**

**5. Go to Experiment design repo you downloaded in step 2.**

   1. Now you are all set to go to the [README](/projects/SoftwareDesign_by_Nikita_Ravi_and_Jonno/Programs/README.md) on how to use the program!

### Linux installation

! Sadly, currently the Linux version on the program doesn't work. Everything is fine until the very last step 4.3 !

The steps on Linux are quite the same as on Windows, apart from the terminal launch. In Linux you need to google how to do that in your distribution. And on step 3 you need to install additional software as said [in this guide](https://reference.digilentinc.com/learn/instrumentation/tutorials/analog-discovery-2-getting-started). When you need to install Adept Runtime(not sdk, but runtime), go [there](https://reference.digilentinc.com/reference/software/adept/start?redirect=1) and download the latest version. To save you time, you can download the Waveforms software(after installing Adept Runtime) from [this](https://mautic.digilentinc.com/waveforms-download) page.

And in step 5 before launching the program comment the lines in BIMBO_Interface.py :

```
myappid = 'BIMBO'
ctypes.windll.shell32.SetCurrentProcessExplicitAppUserModelID(myappid)
```

### MacOS installation

Well, you is going to be the second person who try to run this on mac. This [guide](https://reference.digilentinc.com/learn/instrumentation/tutorials/analog-discovery-2-getting-started) will show you how to install the Waveforms software, other steps are the same as in Windows. Just deleted the following lines in BIMBO_Interface.py
```
myappid = 'BIMBO'
ctypes.windll.shell32.SetCurrentProcessExplicitAppUserModelID(myappid)
```

### Android and IOS

Just install Windows

## Possible problems

It is important to watch where you install your packages. When you open the file in IDE and run it, you do that using some version of Python. If you have only one version of Python in the system, that's the easiest variant, all packages you install will be pinned to this Python version. But if you have multiple versions, the packages you install in one Python version won't be available in another. Why so? When installing packages, Python uses special module called pip. With each version of Python comes it's own pip module. And each pip module installs packages only for it's own version of Python. That's why if you install package in Python 3.6, you won't be able to use it in Python 3.7. Well, technically you probably can by finding in file system all the files of the package and copying them to the folder of another python version and doing something else, but that's a hassle, so we won't consider that.

The possible problem is that when you install Anaconda, it installs its own Python version with it. And you need to ensure that you install packages to the same Python version, which you will use in your IDE to run the python file. This can be easily done by typing command **pip -V** in the terminal, which gives you the full path to your pip module so you can see to which Python version you will install packages with it.

A list of known bugs can be found [here](/projects/SoftwareDesign_by_Nikita_Ravi_and_Jonno/Programs/Bugs.md).

If you really get stuck, you can ask for Ravi's laptop where everything is installed and working. This is only a last resort though.

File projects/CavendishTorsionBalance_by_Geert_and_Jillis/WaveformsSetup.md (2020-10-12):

To setup the Waveforms software correctly please follow the next steps;

1. After opening Waveforms select the "Scope" option from the left sidebar
2. On the right sidebar click on the downward arrow under the "time" settings
3. Set the dropdown after "Settings" to 8192
4. Set the dropdown after "Rate" to 2 Hz. The horizontal axis should read from about -30 to 30 minutes.
5. Under the Channel options, set on both channels the dropdown after "Range" to 200 mV/div.
6. Add a custom math channel and make it record $`\frac{C1-C2}{C1+C2}`$.
7. To start recoding data click the "Scan" button on the top left of the window.
8. To download the data select the "logging" tab on the top of the window, choose the path for where you want to store the data and click the "save" button

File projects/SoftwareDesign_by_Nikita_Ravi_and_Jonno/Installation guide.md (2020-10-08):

The following steps will guide you how to get everything running from scratch (reading [Possible problems](#Possible problems) section recommended)

### Windows installation

1. Go to https://github.com/SanliFaez/labphew

   1. Download the zip archive after pressing the "Code" button
   2. Extract the zip into a place of your choosing

   Another variant how you can get the copy of this repo:
   1.  Open the command prompt. You can open the command prompt by searching "powershell" or "cmd" in windows search. Or type Win+R, type "powershell" or "cmd" and press Enter
   2.  Type **git clone https://github.com/SanliFaez/labphew** . This command will make a copy of this repo in your current folder without need to zip/unzip the repo. You need to have Git installed on your system

2. Install anaconda from: https://www.anaconda.com/products/individual

   1. Open the anaconda prompt by searching "anaconda prompt" in windows
   2. Navigate to your copied repository folder "master-labphew" in the anaconda prompt using ***cd C:/path/to/dir/.../master-labphew*** (you can go up a folder using **cd ..**). Or just copy the path from file explorer and type **cd** and then insert the path
   3. Type ***pip install -e .*** and press Enter
   4. (Do only if use Spyder IDE) Type ***pip install pyqtwebengine*** and press enter *twice* (the second time after the first one is done). This package is needed only for Spyder IDE, without it it won't start

   Or you can do all the same but without installing heavy and slow anaconda. The main benefit which anaconda gives is that it installs Python to you computer. But if you already have Python installed, you probably want to go without anaconda.

   1. Navigate to your copied repository folder "master-labphew" in the command prompt (watch 1 step) using ***cd C:/path/to/dir/.../master-labphew*** (you can go up a folder using **cd ..**). Or just copy the path from file explorer and type **cd** and then insert the path
   2. Type ***pip install -e .*** and press Enter
   3. (Do only if use Spyder IDE) Type ***pip install pyqtwebengine*** and press enter *twice* (the second time after the first one is done). This package is needed only for Spyder IDE, without it it won't start

3. Download and install Waveforms program from: https://mautic.digilentinc.com/asset/110:waveforms-windows-64-bit-download. Agree to default options. The detailed guide(on Windows you don't need it) is [there](https://reference.digilentinc.com/learn/instrumentation/tutorials/analog-discovery-2-getting-started)

4. Go to https://git.science.uu.nl/ued2020/experiment-design-2020

   1. Download a zip of the repository. Extract the zip. Or you can do the same via Git as with labphew
   2. Go to experiment-design-2020/projects/SoftwareDesign_by_Nikita_Ravi_and_Jonno/Programs/ folder
   3. Open the BIMBO_Interface.py in the Programs folder using Spyder or PyCharm or any other IDE and run the file. You can move the Programs folder to wherever you want
   4. Enjoy the program

### Linux installation

! Sadly, currently the Linux version on the program doesn't work. Everything is fine until the very last step 4.3 !

The steps on Linux are quite the same as on Windows, apart from the terminal launch. In Linux you need to google how to do that in your distribution. And on step 3 you need to install additional software as said [in this guide](https://reference.digilentinc.com/learn/instrumentation/tutorials/analog-discovery-2-getting-started). When you need to install Adept Runtime(not sdk, but runtime), go [there](https://reference.digilentinc.com/reference/software/adept/start?redirect=1) and download the latest version. To save you time, you can download the Waveforms software(after installing Adept Runtime) from [this](https://mautic.digilentinc.com/waveforms-download) page.

And in step 4 before launching the program comment the lines in BIMBO_Interface.py :

```
myappid = 'BIMBO'
ctypes.windll.shell32.SetCurrentProcessExplicitAppUserModelID(myappid)
```

### MacOS installation

Well, you is going to be the first person who try to run this on mac. This [guide](https://reference.digilentinc.com/learn/instrumentation/tutorials/analog-discovery-2-getting-started) will show you how to install the Waveforms software, other steps are the same as in Windows.

### Android and IOS

Just install Windows

## Possible problems

It is important to watch where you install your packages. When you open the file in IDE and run it, you do that using some version of Python. If you have only one version of Python in the system, that's the easiest variant, all packages you install will be pinned to this Python version. But if you have multiple versions, the packages you install in one Python version won't be available in another. Why so? When installing packages, Python uses special module called pip. With each version of Python comes it's own pip module. And each pip module installs packages only for it's own version of Python. That's why if you install package in Python 3.6, you won't be able to use it in Python 3.7. Well, technically you probably can by finding in file system all the files of the package and copying them to the folder of another python version and doing something else, but that's a hassle, so we won't consider that.

The possible problem is that when you install Anaconda, it installs its own Python version with it. And you need to ensure that you install packages to the same Python version, which you will use in your IDE to run the python file. This can be easily done by typing command **pip -V** in the terminal, which gives you the full path to your pip module so you can see to which Python version you will install packages with it.

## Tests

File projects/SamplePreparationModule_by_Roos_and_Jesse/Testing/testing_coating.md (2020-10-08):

Your workspace needs to be chemically resistant so that it doesn't get destroyed by the first small spill. We applied to layers of polyurethane coating to provide this chemical resistance. In order to test how good this actually protects your workspace we dropped various solvents and acids on a piece of testing wood that has the same polyurethane coating to see how resistant it actually is. Typically you would clean up within 5 minutes after spilling something so everything was left on for 5 minutes. The solvents that have been tested are:
- ethanol: No visible damage -> feel test after 24 hours
- acetone: No visible damage -> feel test after 24 hours
- toluene: No visible damage -> feel test after 24 hours
Most of these solvents evaporate pretty quickly especially toluene, which was completely gone after 5 minutes. The reason for leaving it 24 hours is that some of the solvent may have moved into the coating. Touching it at this point may be dangerous for yourself and it will still have an effect on the final result, therefore leave it for 24 hours. 

Two different acid concentration series have been tested: Hydrochloric acid and nitric acid. 
The following concentrations have been measured:
- 10 % obtained by adding 1 ml of acid (100 %) to 9 ml of demiwater.
- 25 % obtained by adding 2.5 ml of acid (100 %) to 7.5 ml of demiwater.
- 50 % obtained by adding 5ml of acid (100 %) to 5ml of demiwater.
- 100 % taken from container that is available in the lab.
Note that the percentages here are based on the concentration that is available in the lab. We have used the standard university concentrations which are about 40 %, according to the lab assistant.
Prepare the samples by using a Finn pipet. For instructions on how to use a Finn pipet click [here](https://git.science.uu.nl/ued2020/experiment-design-2020/-/blob/master/projects/SamplePreparationModule_by_Roos_and_Jesse/peer_instructions/intructions.md) Keep in mind to always add the acid to the water and before dropping it onto the wood stir it with a pasteur pipet (simpler version of a Finn pipet). Take a clean pasteur pipet after each time you dripped some acid onto the wood to avoid messing up your concentrations.
Also leave these samples on the wood for approximately 5 minutes and the remove them with an pasteur pipet.

Finally [aqua regia](https://git.science.uu.nl/ued2020/experiment-design-2020/-/blob/master/projects/SamplePreparationModule_by_Roos_and_Jesse/peer_instructions/intructions.md) has been prepared and dropped onto the wood. This has only been done for the 100 % concentration, since it contains both Nitric and Hydrochloric acid.

### Conclusion
#### Visual
When looking at the wood after 24 hours we can only see damage where 100 % Nitric acid and Aqua Regia have been. These were also already visible after having the acid on the coating for 24 hours. In the [picture](https://git.science.uu.nl/ued2020/experiment-design-2020/-/blob/master/projects/SamplePreparationModule_by_Roos_and_Jesse/Photos/results_acid_test.jpg) the damage is also visible.

#### Feel test
None of the Hydrochloric acid concentrations had any effect on the coating. For the Nitric acid only the 100 % feels slightly different. It feels a bit smoother. Ethanol didn't have an effect on the coating, nor did toluene. For acetone it is hard to say, the wood feels slightly smoother here, which may be the result of the test, but it may also just be a smoother area. 
The region where Aqua Regia has been also feels smoother.
Most importantly though is that while the coating is slightly smoother or has a different colour none of the acids or solvents actually destroyed the wood. Maybe spilling a lot of acid is not a good idea, especially on the long term, but you don't have to worry about the workspace being unusable after have spilled something several times.

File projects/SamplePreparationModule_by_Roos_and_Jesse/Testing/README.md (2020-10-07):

In this directory you can find all files regarding the testing of the finished box

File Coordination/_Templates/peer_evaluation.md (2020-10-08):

# Reproducibility report

## Experiment/team: 
_the experiment that is reproduced and its owners_

## Reviewers: 

## Report 

### Documentation:

1.	Could you understand the purpose of the experiment? Explain.
2.	Were the safety instructions clear?
3.	How helpful is the documentation for reproducing the measurement?
4.	Did you get stuck at some point? What extra help did you need to proceed?
5.	Are you guided to reproduce previous measurements? How easily could you navigate through the project documentation?
6.	What can be improved in the documentation?

### Measurements:

1.	Can you operate the setup with the provided instructions? 
2.	How close were the results you obtain to the previously reported results?
3.	Can you understand and explain the analysis procedure to a third person?
4.	Is the setup robust and safe to operate? 
5.	Did you encounter any issues? Could you troubleshoot those without contacting the owners?
6.	What part of the measurement procedure did you appreciate most?

### Interactions:

1.	Could you relate to the stated goal of the project?
2.	Which instructions did you need from the owners on top of the written files?
3.	Does the experiment accomplish its stated purpose?
4.	What do you recommend to the project owners to improve their complete package?

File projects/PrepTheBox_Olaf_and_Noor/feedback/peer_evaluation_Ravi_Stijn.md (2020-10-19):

# Reproducibility report

## Experiment/team:   
PrepTheBox by Noor and Olaf

## Reviewers:   
Stijn and Ravi

## Report 

### Documentation:

**1.	Could you understand the purpose of the experiment? Explain.**  
    It's not really explained why this experiment shows that the design of the box leads to a properly functional box. We did understand that you had to ask other groups what they wanted to show that it had all of these features.

**2.	Were the safety instructions clear?**  
    Yes, but it is still very hard to open the box. The front panel is missing some form of handle. It also says your laptop is in the box during the experiment, but this is not true.  

**3.	How helpful is the documentation for reproducing the measurement?**  
    Reproducing is quite easy with the documentation, but be a little more specific on where exactly you want to put the sensor/beakers. Unclear how to raise the right panel. We made a guess.

**4.	Did you get stuck at some point? What extra help did you need to proceed?**  
    Not really clear what you need the USBlogger for in the beginning but we figured it out. 

**5.	Are you guided to reproduce previous measurements? How easily could you navigate through the project documentation?**  
    The README does guide you to the previous measurements.

**6.	What can be improved in the documentation?**  
    Be more clear on the exact setup of the experiment such as placement of the sensor/beakers. Also, add a list of what people want for the box, because this is not reproducible if we do not know what they told you.

### Measurements:

**1.	Can you operate the setup with the provided instructions?**  
    Be a little more specific on where exactly you want to put the sensor/beakers. 

**2.	How close were the results you obtain to the previously reported results?**    
    Our result for the closed box was not what was previously reported. Our graph can be found [here](projects/PrepTheBox_Olaf_and_Noor/feedback/GraphBox.jpeg)

**3.	Can you understand and explain the analysis procedure to a third person?**  
    Yes.

**4.	Is the setup robust and safe to operate?**  
    Ravi cut his fingers. Handles on the front panel would be nice.

**5.	Did you encounter any issues? Could you troubleshoot those without contacting the owners?**  
    We did have some issues but could figure it out on our own.

**6.	What part of the measurement procedure did you appreciate most?**  
    The simplicity was very nice.

### Interactions:
 
**1.	Could you relate to the stated goal of the project?**  
    Yes it would be nice to have a box with all features implemented.

**2.	Which instructions did you need from the owners on top of the written files?**  
    Nothing.

**3.	Does the experiment accomplish its stated purpose?**  
    Not really. We did not clearly understand what the goal was. Also, there was no way to check whether the features people asked for were implemented, because there was no list of what they initially asked for. Would be nice to be able check what you heard from people.
    
**4.	What do you recommend to the project owners to improve their complete package?**  
    Implement what people asked for a bit better. For example, there need to be holes for cables and such to the outside of the box. Also implement handles on the front for better handling of the box.

## Reaction from the Prep The Box team

Hi Ravi and Stijn! First of all thanks a lot for the provided feedback. 

It is true that some of the elements from the design are not yet implemented in the box. It still is a work in progress of course (for example the holes in the bottom are still on our to-do list but there has not yet been time to implement this). The idea on handles on the front panel is a good one. This will surely be added to the overal design. 

We also understand better thanks to your feedback that the instructions were a bit unclear on some parts. We will address this problem by adding some lines of instructions on the spots where you encountered some issues.
    
The idea of asking the other groups what they needed was not to check a list of demands, but to check our design (and not the not-finished product). We wanted you to read through and get a feeling on the design of the box and then see if based on the demands of the other groups, you would get to the same or a similar design as ours or perhaps to an entirely different design. This was an "experiment" entirely separate from the temperature measurment, which was an experiment to quantitatively check one specific part of the design. We will naturaly make this more clear in our improved version of the instructions.

Thank you again for taking the time to perform this experiment and provide this feedback. It helps us a lot to improve the project and it makes clear how to proceed.

Kind regards, Olaf and Noor

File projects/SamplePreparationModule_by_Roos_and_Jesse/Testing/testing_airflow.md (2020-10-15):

### Testing airflow
We tested the airflow of the box by using an anemometer.
Pascal provided us with 3 kinds of anemometers, one from [travel&co](https://git.science.uu.nl/ued2020/experiment-design-2020/-/blob/master/projects/SamplePreparationModule_by_Roos_and_Jesse/Photos/Travel_co_anemometer.jpeg), one from [testo](https://git.science.uu.nl/ued2020/experiment-design-2020/-/blob/master/projects/SamplePreparationModule_by_Roos_and_Jesse/Photos/testo_anemometer.jpeg) and a [kaindl windmaster 2](https://git.science.uu.nl/ued2020/experiment-design-2020/-/blob/master/projects/SamplePreparationModule_by_Roos_and_Jesse/Photos/kaindl_anemometer.jpeg). 
The testo anemometer was the most accurate one and was therefore used for most of the measurements.
In the table underneath you can find the values for the windspeed we measured.
When the anemometer was in place, we waited a bit until the value for the windspeed stabalized a bit. 
After waiting for a while, the value on the anemometer still fluctuated a lot.
We think this might be due to the fan not rotating continuously.
Because of the fluctuations, an error of +- 0.1 should be taken into account for all measurements.
All measurements were taken with the sash fully opened unless mentioned ontherwise.

#### table 1: Measured windspeed values for different positions in and around the box.
|position|windspeed (m/s)|
| ------ | -------- |
|in the room we were measuring in| 0.00|
|sides of the box without ductape| 0.00|
|sides of top window|0.00|
|sides of front window|0.00|
|end of the pipe (testo)| 1.60|
|end of the pipe (kaindl)| 1.7|
|end of the pipe (travel&co)| 1.6|
|front of sash while fully opened|0.20|
|front of sash when almost closed|1.12|
|middle of hood| 0.23|
|right middle of hood| 0.04|
|left middle of hood| 0.04|
|inside hood right below fan| 0.66|
|inside hood side of fan| 0.52|

Based on these results there is no airflow through the sides of the box.
However, because of the large error of the anemometer and for extra safety we decided to tape the sides of the box with ductape anyway.

According to [this](https://www.nationallaboratorysales.com/blog/what-is-the-importance-of-fume-hood-face-velocity/) website, the face velocity of a fume hood should be between 0.3 m/s and 0.5 m/s. The face velocity is the airvelocity going through the opening of the fumehood while it is fully opened. This corresponds to the measurement with the front of the sash fully opened, which was 0.20 m/s. This means that our fan is actually a little weak according to fume hood regulations. However, experiments that actually require this face velocity in order to be safe should be performed in an actual certified fume hood. For the purpose of preparing samples that are kept in usual solvents, a face velocity of 0.20 m/s is safe enough.

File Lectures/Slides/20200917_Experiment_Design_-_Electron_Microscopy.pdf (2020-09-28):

17/09/2020

### Daring to Try

# Electron Microscopy

Dr. Gerhard A. Blab
Molecular Biophysics

EXPERIMENT DESIGN

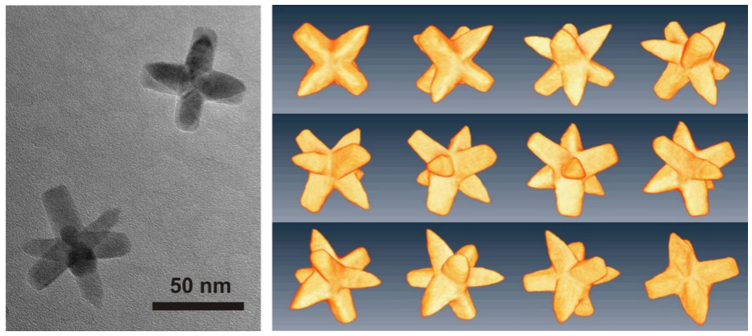
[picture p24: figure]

Slides & images by Profs. Gerritsen, van Huis, and the Internet

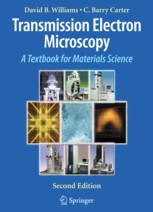
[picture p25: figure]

### Shameless Plug for “Advanced Microscopy”

17/09/2020 3

- Transmission Electron Microscopy
- Williams and Carter

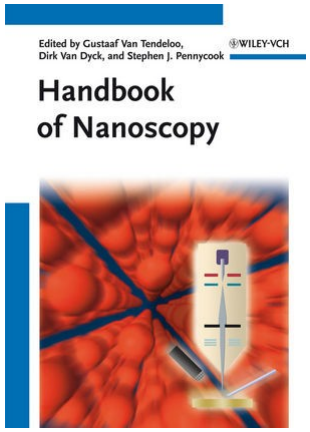
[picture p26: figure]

- Handbook of Nanoscopy
- Van Tendeloo et al. (Eds).
- EELS Atlas
Reading list for
NS-EX423M
Advanced Microscopy
Block 2

16/09/2020

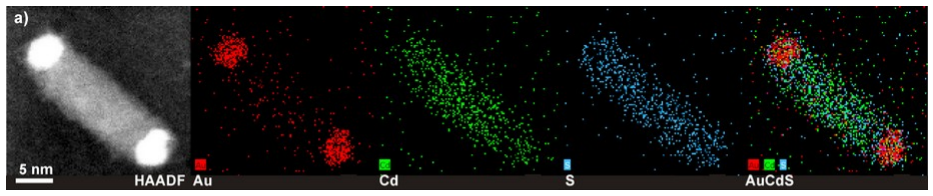
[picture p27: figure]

### Daring to Try

# Electron Microscopy

## Part 1: History

Dr. Gerhard A. Blab
Molecular Biophysics

EXPERIMENT DESIGN

Slides & images by Profs. Gerritsen, van Huis, and the Internet

## Ridiculously Abridged History of Optics & Microscopy

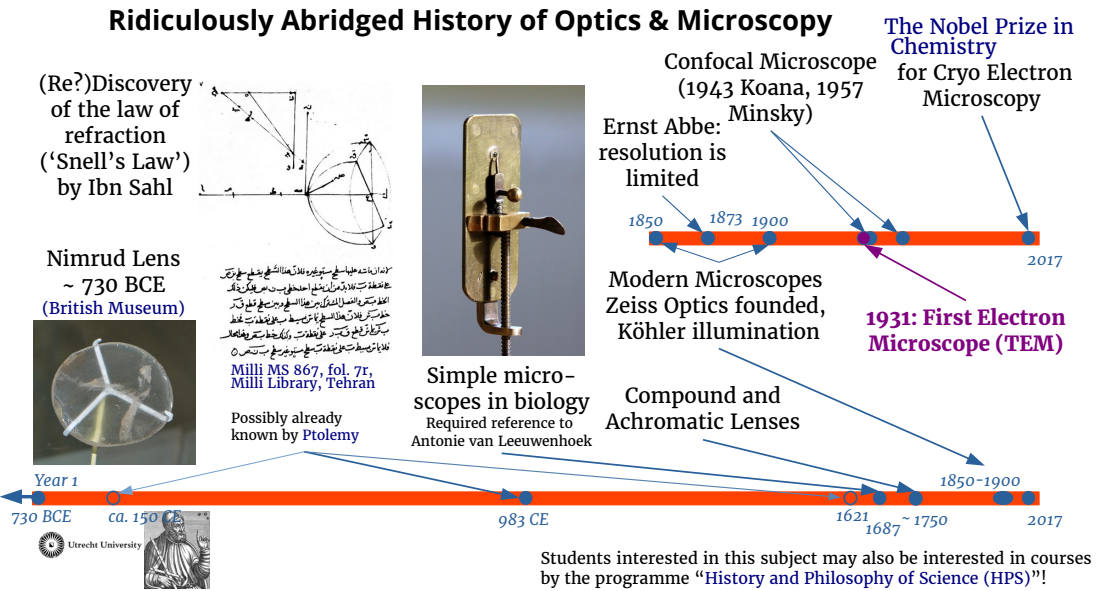
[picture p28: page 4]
Nimrud Lens ~ 730 BCE (British Museum); 730 BCE; Year 1; Compound and Achromatic Lenses; Confocal Microscope (1943 Koana, 1957 Minsky); Ernst Abbe: resolution is limited; 1931: First Electron Microscope (TEM)

The Nobel Prize in
Chemistry
for Cryo Electron
Microscopy

(Re?)Discovery
of the law of
refraction
(‘Snell’s Law’)
by Ibn Sahl

Modern Microscopes
Zeiss Optics founded,
Köhler illumination

Milli MS 867, fol. 7r,
Milli Library, Tehran

Simple micro-
scopes in biology
Required reference to
Antonie van Leeuwenhoek

Possibly already
known by Ptolemy

Students interested in this subject may also be interested in courses
by the programme “History and Philosophy of Science (HPS)”!

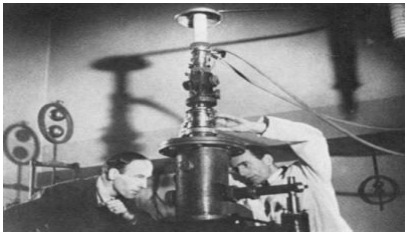
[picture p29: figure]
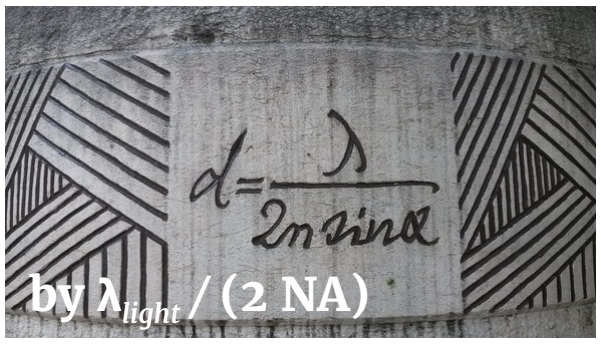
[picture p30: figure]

6

## Electron Microscopy

Electrons:

Particles
Mass m = 9.109 × 10⁻³¹ kg
Charge q = -1.602 x 10⁻¹⁹ C (-e)

Waves
Ernst Abbe (1873) resolution optical microscope limited by λlight / (2 NA) De Broglie (1924) h = λe pe
| (h Plank’s constant, p momentum), h = 6.63 10⁻³⁴ Js

First electron microscope, Ernst Ruska 1931

## EM application areas:

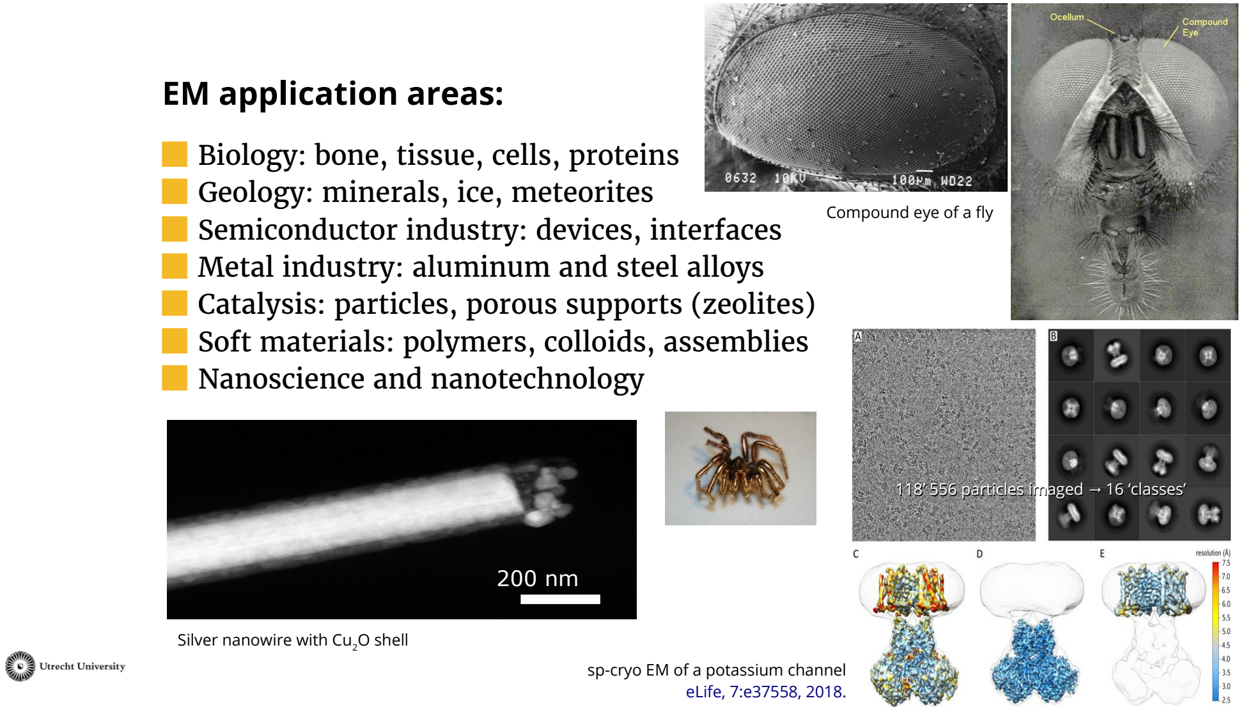
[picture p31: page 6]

- Biology: bone, tissue, cells, proteins
- Geology: minerals, ice, meteorites
- Semiconductor industry: devices, interfaces
- Metal industry: aluminum and steel alloys
- Catalysis: particles, porous supports (zeolites)
- Soft materials: polymers, colloids, assemblies
- Nanoscience and nanotechnology

200 nm

sp-cryo EM of a potassium channel eLife, 7:e37558, 2018.

Compound eye of a fly

Silver nanowire with Cu2O shell

118’ 556 particles imaged 16 ‘classes’ →

16/09/2020

### Daring to Try

# Electron Microscopy

## Part 2: Physics & Engineering

Dr. Gerhard A. Blab
Molecular Biophysics

EXPERIMENT DESIGN

Slides & images by Profs. Gerritsen, van Huis, and the Internet

## Transmission Electron Microscope (TEM) & Scanning Electron Microscope (SEM)

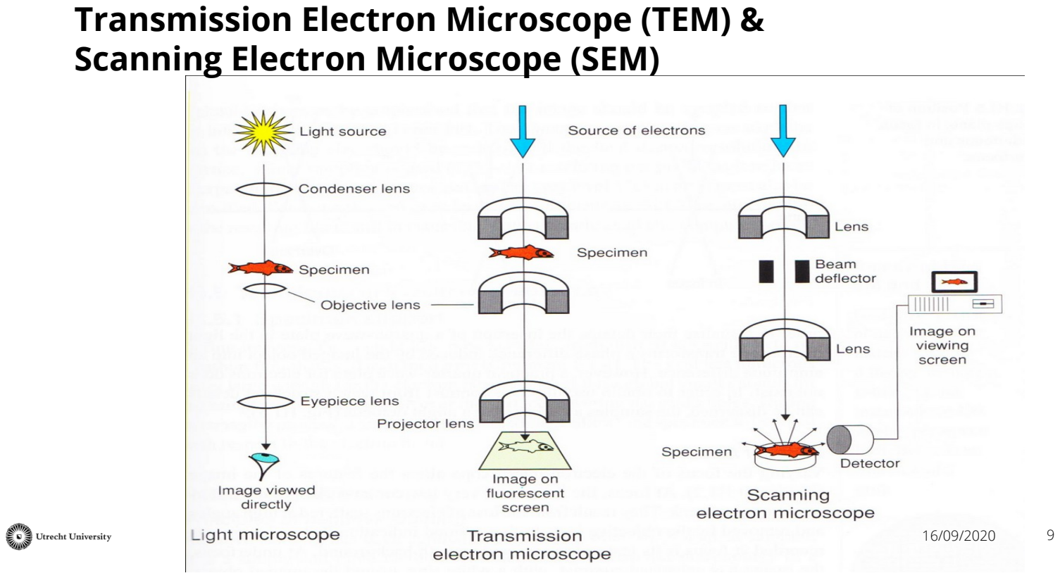
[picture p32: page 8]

16/09/2020 9

## Transmission Electron Microscope (TEM) & Scanning Electron Microscope (SEM)

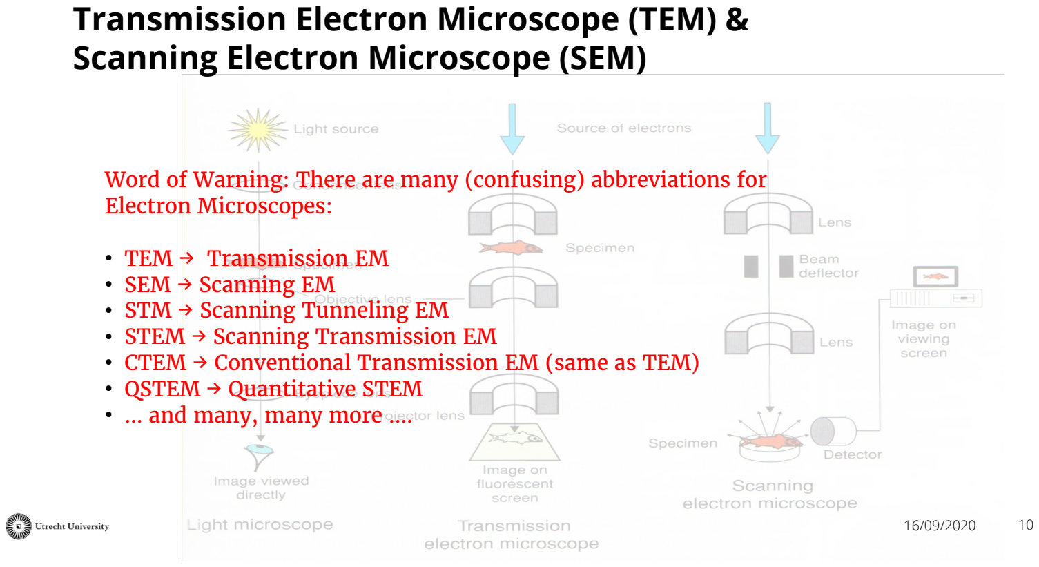
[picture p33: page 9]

16/09/2020 10

Word of Warning: There are many (confusing) abbreviations for Electron Microscopes:

- TEM → Transmission EM
- SEM → Scanning EM
- STM → Scanning Tunneling EM
- STEM → Scanning Transmission EM
- CTEM → Conventional Transmission EM (same as TEM)
- QSTEM → Quantitative STEM
- … and many, many more ….

11

## Wave character of the electron

Wavelength electron: λe = h/pe , with pe= me ve

,

and h Planck’s constant

Electron in an electric field with potential difference U

Accelerated up to eU = ½ mev
2

= ½ pe

2/me (Epot = Ekin)

➔
➔ | (U in Volt)
Typical EM U ~ 40 – 400 keV | λe

= 0.06 – 0.019 Å, with typical resolution ~ λ however achievable resolution is 100× worse than this ...

Relativistic effects cannot be neglected:
100 keV 0.55 c →

pe

=√2me
eU
λ e

=

h
√2me
eU

≈

12
√U

[ Å]

12

## Focusing of electrons

### Lorentz force: F = q (v × B) (F ┴ B, v)

### Electron spirals around field lines

### Electrons can be focused by magnetic field


Busch (1926),

### 5 years before EM


13

## Resolution EM

For diffraction limited resolution: d ~ λe / sin θ In EM, θ is very small

EMs not diffraction limited
Astigmatism & spherical aberration
In practice (spherical) aberrations dominate the resolution d = (Cs λe

3)
1/4
Cs

spherical aberration coefficient common value of ~ 1 mm = 10⁷ Å d = 5 Å (100 keV)

Practical resolution:
biological specimens: 2-5 nm but possibly down to 3 Å. material science: d <0.1 nm ( atomic resolution )

Single graphene sheet
@ 200 keV

## Imaging Modes


Bright-field TEM
(BF-TEM, aperture)

Dark-field STEM
(DF-STEM, annular detector)

Scanning Electron Microscope (SEM, secondary electrons)

Fluorescence
(simulated)

## EM: Electrons Interact With the Sample

- Different qualities of
interaction:
- Topographic (surface)
- Atomic Number
- Luminescence (electronic states)


- X-Ray or Auger Electrons – atomic composition
- Elastic and Inelastic
Processes
- Sample will be damaged by the imaging process!

## TEM image formation – contrast modes

- Mass-thickness contrast

I=I0 exp(σ·t)

t is sample thickness
σ is material-dependent scattering cross-section

## BF-TEM imaging issues – Phase Information

underfocus | overfocus

The focus manipulates the phase information, and can make the dots (columns of atoms) in HR images look either black or white.

S. Takeda et al, Ultramicroscopy (in press)

HAADF

## Scattering in STEM mode: BF, ADF and HAADF

- Which electrons are detected with HAADF-STEM?
- Only strongly scattered electrons, mostly elastic Rayleigh scattering
- Quantitatively sensitive to the atomic element, so-called Z contrast:
I ~ Z
2
- Not sensitive to light elements Z<10 (cutoff)

## Electron Diffraction


Amorphous Au | Single Crystal Au | Polycrystalline Au

20

## Specimen preparation

Specimen preparation critical

Biological molecules are not electron dense (CNO – Z = 6, 7, 8!)
Staining: Treatment with heavy metals (Uranyl acetate, Osmium tetraoxide) Label proteins of interest using antibodies + nanogold particles

Negative staining: Embed specimen in electron dense medium


17/09/2020

### Daring to Try

# Electron Microscopy

## Part 3: The Nobel Prize

Dr. Gerhard A. Blab
Molecular Biophysics

EXPERIMENT DESIGN

Slides & images by Profs. Gerritsen, van Huis, and the Internet

22

### Cryo-EM (TEM)

Cryo-EM:
- Rapid cooling in e.g. liquid nitrogen
- Preserves native structures, reduces radiation damage
- No staining required (but noisier images)
- Flash cooling in liquid ethane or propane (<< 77 K) avoids ice crystals (vitreous ice)
- Some measurements done at 4 K.


RNA-DNA hybrids vitreous ice by cryo-EM. Inner diameter ~33 Å and outer diameter ~ 166 Å.


Cryo-EM image SUV.

23

## Single particle cryo imaging

- Many particles imaged at ‘random’ orientations

bacteriophage MS2 (cryo-EM) (virus that infects bacteria)

## Single particle cryo imaging


24

- Many particles imaged at ‘random’ orientations
- Smart averaging of
particles with same
orientation (use
symmetry), pattern
recognition

➔ Determine 3-D structure
from projections of
different orientations

bacteriophage MS2

### 2017 Nobel Prize Cryo EM

“for the developing cryo-electron microscopy for the high resolution
structure | determination | of
biomolecules in solution.”

●

Jacques Dubochet

●

Joachim Frank
- Richard Henderson

link:
The Nobel Prize in Chemistry 2017

17/09/2020 25

Source: Serious Science Channel “Single-Particle Electron Microscopy – Richard Henderson” Link: Youtube

# Video Discussion (https://www.youtube.com/watch?v=j_sfs6uwWlc)

17/09/2020 26

Direct Electron Detectors

DOI 10.1016/bs.mie.2016.05.056 McMullan, Farqui, and H enderson; Methods in Enzymology

Discovery vs. Invention

Gradual Improvement of
Original Idea

Technological (https://www.youtube.com/watch?v=j_sfs6uwWlc) Improvement vs. Methodological (https://www.youtube.com/watch?v=j_sfs6uwWlc) Improvement

Everything has been studied, (https://www.nobelprize.org/list-of-2017-nobel-laureates/) end of Structural Biology?

Gradual Grow vs Hype
People start to use method / it (https://www.youtube.com/watch?v=j_sfs6uwWlc) can become useful to them

Many (https://www.youtube.com/watch?v=j_sfs6uwWlc) (small) ideas have to come together

17/09/2020

### Daring to Try

# Electron Microscopy

## Part 4: The Future

Dr. Gerhard A. Blab
Molecular Biophysics

EXPERIMENT DESIGN

Slides & images by Profs. Gerritsen, van Huis, and the Internet

## Environmental TEM (E-TEM)

- Create a gas environment very close to the specimen (pressure ~ 1 mbar)
- Use a differential pumping system to prevent that the electrons have to travel through a long gas column (degrading the resolution)

## Environmental TEM


- Example:

Dynamic changes at the
surface of cerium oxide
nanoparticles during redox reactions
- Gas environment of 0.5 Torr (0.7 mbar) of H2

P.A. Crozier et al, Ultramicroscopy 108 (2008) 1432

270 °C

730 °C

600 °C

## Liquid cell TEM


- Study self-assembly (SA)
in confined geometries
- Utrecht University:
- Group Marijn van Huis (3D)
- Group Daniel Vanmaekelbergh (2D)
- 3D and 2D assembly: TEM studies
- Group Sara Bals, Staf van Tendeloo (Antwerp)

Not an EM image

Self-assembly in Liquid Cell TEM

- Self-ordering of octapods into strings

Figure 2 from:
E. Sutter, L. Manna et al.,
In situ microscopy of the self-assembly of branched nanocrystals in solution
Nature Commun. 7 (2016) 11213 DOI: 10.1038/ncomms11213

Scale bar: 500 nm
STEM in solution

movie: https://www.nature.com/articles/ncomms11213#Sec11

# Correlative Microscopy

Standard correlative microscopy in 2 setups

Fluorescence microscope: identify regions of interest EM: image ultrastructure


# Integrated Light and Electron Microscopy


TEM

FM

Karreman et al., DOI: 10.1369/0022155412473756 and unpublished data Muscle tissue

# Integrated Light and Electron Microscopy

TEM

FM

Karreman et al., DOI: 10.1369/0022155412473756 (https://dx.doi.org/10.1369/0022155412473756) and unpublished data

© Utrecht University

The information in this presentation has been compiled with the utmost care, but no rights can be derived from its contents.

DISCLAIMER

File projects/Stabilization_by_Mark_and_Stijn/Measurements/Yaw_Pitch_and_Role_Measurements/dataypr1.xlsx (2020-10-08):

Table 1
 | ∆oog | 0.01666666667
 | tafel recht |  |  |  |  |  |  | tafel hoek
 | oog | y | p | r | r corrected | oog-corrected | p corrected
 | 0 | -6.34 | -0.04 | 0.04 | 0.04 | 0.04 | -0.04
 | 1 | -6.44 | -0.04 | 1.05 | 1.05 | 0.05 | -0.04
 | 2 | -6.66 | -0.03 | 2.06 | 2.06 | 0.06 | -0.03
 | 3 | -6.71 | -0.01 | 3.04 | 3.04 | 0.04 | -0.01
 | 4 | -6.8 | -0.02 | 4.07 | 4.07 | 0.07 | -0.02
 | 5 | -6.88 | -0.01 | 5.04 | 5.04 | 0.04 | -0.01
 | 6 | -6.93 | 0.01 | 6.02 | 6.02 | 0.02 | 0.01
 | 7 | -6.94 | 0.01 | 7.04 | 7.04 | 0.04 | 0.01
 | 8 | -7 | 0.02 | 8.06 | 8.06 | 0.06 | 0.02
 | 9 | -7.43 | 0.05 | 9.05 | 9.05 | 0.05 | 0.05
 | 10 | -7.59 | 0.04 | 10.05 | 10.05 | 0.05 | 0.04
 | 15 | -8.33 | 0.12 | 14.99 | 14.99 | -0.01 | 0.12
 | 20 | -8.25 | 0.18 | 20.1 | 20.1 | 0.1 | 0.18
 | 25 | -8.13 | 0.24 | 25.08 | 25.08 | 0.08 | 0.24
 | 30 | -7.99 | 0.32 | 20.12 | 30.12 | 0.12 | 0.32
 | 35 | -7.76 | 0.42 | 35.18 | 35.18 | 0.18 | 0.42
 | 40 | -7.55 | 0.5 | 40.22 | 40.22 | 0.22 | 0.5
 | 45 | -7.15 | 0.61 | 45.29 | 45.29 | 0.29 | 0.61
 | 50 | -6.75 | 0.71 | 50.31 | 50.31 | 0.31 | 0.71
 | 55 | -6.23 | 0.79 | 55.36 | 55.36 | 0.36 | 0.79
 | 60 | -5.69 | 0.9 | 60.42 | 60.42 | 0.42 | 0.9
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

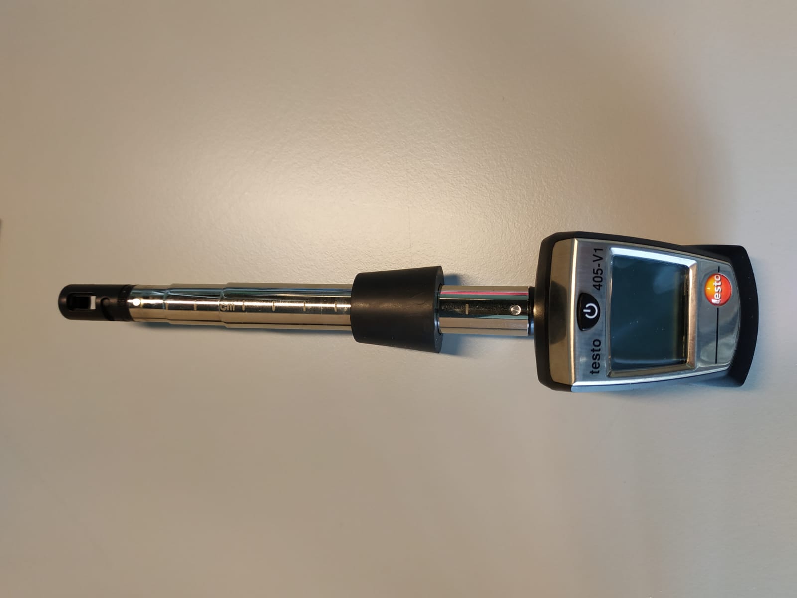
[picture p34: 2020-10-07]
projects/SamplePreparationModule_by_Roos_and_Jesse/Photos/testo_anemometer.jpeg

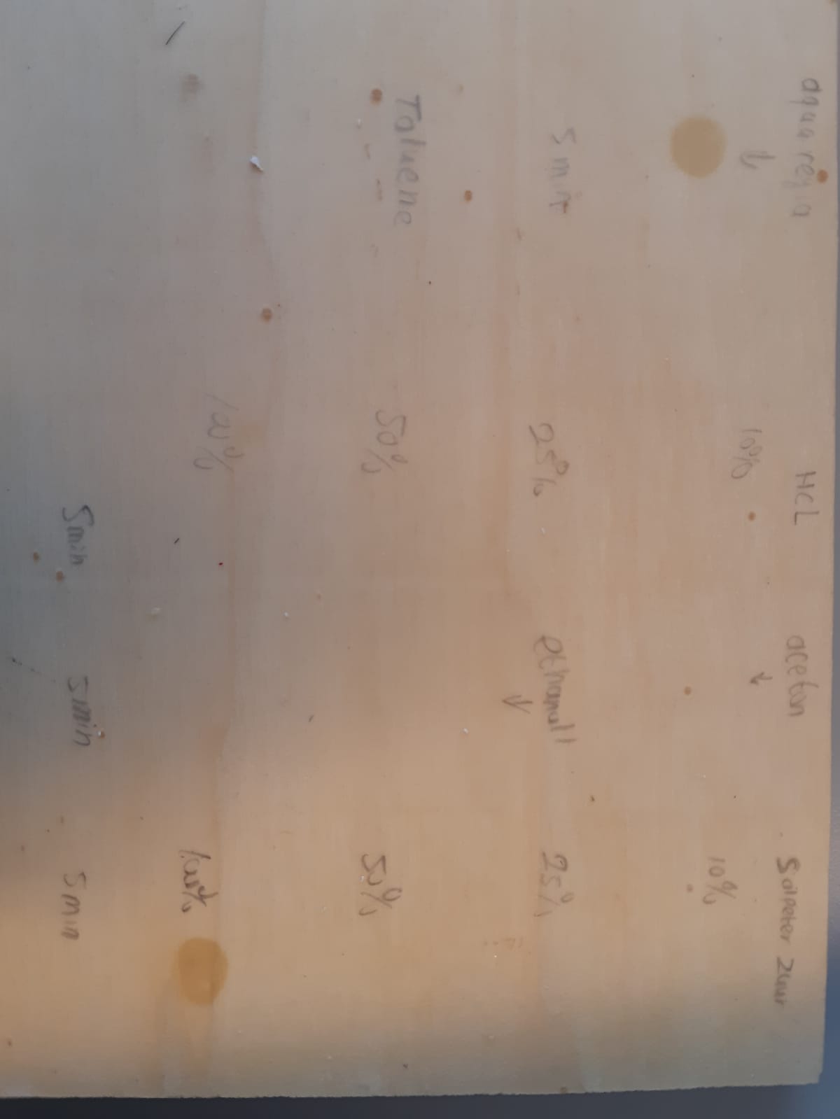
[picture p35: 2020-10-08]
projects/SamplePreparationModule_by_Roos_and_Jesse/Photos/results_acid_test.jpg

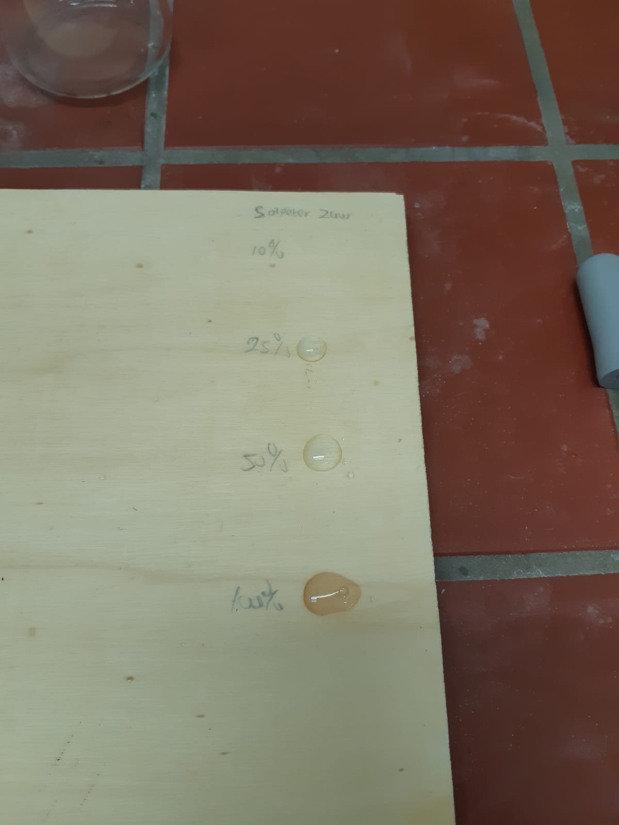
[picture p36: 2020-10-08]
projects/SamplePreparationModule_by_Roos_and_Jesse/Photos/Acid_testing.jpg

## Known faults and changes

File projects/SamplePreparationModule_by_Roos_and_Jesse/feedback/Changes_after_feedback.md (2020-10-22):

### Feedback Processing

We want to thank the group for the helpful feedback.
We added extra links to the readme's in order to help with navigation through the folders. Our initial idea was to enable people to browse through the different directories, but for people that are just interested in certain aspects it might indeed be nice to have additional links that bring them straight to where to want to be.
We also improved on the readme in the instructions directory. We first aimed to a process in which the reproduction of the experiment could be done by following the exact same steps as we have performed. This required a lot of additional navigation however. We have now included how to perform the testing in the readme in the hope that people don't feel quite as lost when they are looking at our directory. We have not removed the safety information from the seperate file along with some additional tutorial instructions, in order to stress people to go there to read the safety instructions carefully. In our experience, if you add the safety instructions in the same file people will just quickly skim over it and not really take it in consideration while performing the experiment. By forcing the group the go to a different file to read the safety instructions we hope that they will read them properly and remember them while performing the experiment.
We also added some additional information to the safety instructions in order to make them apply to a wider audience. We specifically included what to do in case something goes wrong so people without knowledge of chemicals know what to do in case something goes wrong. 
We also specified the locations for the ventilation testing a bit better, hopefully this will improve the re-testability of the box. We should have mentioned that testing locations now covered with duct tape would not be neccessary since we don't plan to take the duct tape of.

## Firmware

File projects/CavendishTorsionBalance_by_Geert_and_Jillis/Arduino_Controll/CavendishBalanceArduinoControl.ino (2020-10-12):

#include <Servo.h>



Servo bigServo;                 // providing a name

int ballsDelay = 2400;          // Timelength to move balls from counterclockwise to clockwise position (and vice versa)



int incomingByte = 0; // for incoming serial data
int toServo = 0;      // to send to servo
int stateBalls = 0;   // 0 for center, 1 for fully left, -1 for fully right

void setup()
{
  bigServo.attach(3);
  // Open serial communications and wait for port to open:
  Serial.begin(9600);
  while (!Serial) {
    ; // wait for serial port to connect. Needed for Native USB only
  }

  Serial.print("Hello world.");
}



void loop() {
  // send data only when you receive data:
  if (Serial.available() > 0) {
    // read the incoming byte:
    incomingByte = Serial.read();

    // say what you got:
    Serial.print("I received: ");
    Serial.println(incomingByte);

    if(incomingByte == 83 && stateBalls == 0){ //Start from 0 position, go to the "+1" position on input S
      Serial.print("Start");
      Serial.println();
      int localDelay = ballsDelay / 2;
      toServo = 180;
      bigServo.write(toServo);
      toServo = 90;
      delay(localDelay);
      bigServo.write(toServo);
      stateBalls = 1;
    }

    else if(incomingByte == 69){ //Go from any position back to the neutral position on input E
      Serial.print("End");
      Serial.println();
      int localDelay = ballsDelay / 2;
      if (stateBalls == 1){toServo = 0;}
      else if (stateBalls == -1) {toServo = 180;}
      bigServo.write(toServo);
      toServo = 90;
      delay(localDelay);
      bigServo.write(toServo);
      stateBalls = 0;
    }
    
    else if(incomingByte == 82 && stateBalls == 1){ //Go to the "-1" position on input R
      Serial.print("Go right");
      Serial.println();
      toServo = 0;
      bigServo.write(toServo);
      toServo = 90;
      delay(ballsDelay);
      bigServo.write(toServo);
      stateBalls = -1;
    }
    
    else if(incomingByte == 76 && stateBalls == -1){ //Go to the "+1" position on input L
      Serial.print("Go left");
      Serial.println();
      toServo = 180;
      bigServo.write(toServo);
      toServo = 90;
      delay(ballsDelay);
      bigServo.write(toServo);
      stateBalls = 1;
    }

    
    else if(incomingByte == 108 ){ //finetune the position in "+1" direction on input l
      Serial.print("Go Left");
      Serial.println();
      toServo = 180;
      bigServo.write(toServo);
      toServo = 90;
      int localDelay = 100;
      delay(localDelay);
      bigServo.write(toServo);
    }    
    else if(incomingByte == 114){ //finetune the position in "-1" direction on input r
      Serial.print("Go Left");
      Serial.println();
      toServo = 0;
      bigServo.write(toServo);
      toServo = 90;
      int localDelay = 100;
      delay(localDelay);
      bigServo.write(toServo);
    }

  }
}

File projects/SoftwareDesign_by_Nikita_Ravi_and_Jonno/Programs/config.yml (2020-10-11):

# parameters for the scan go here
scan:
  filename:         'C:\Users\nikza\Desktop\something.csv'
  title:             Scan
  title1:            AI Channel 1
  title2:            AI Channel 2
  duration:         10
  start:            0     # (V)
  stop:             5     # (V)
  step:             0.04  # (V)
  test:             False
  test2:            True
  x_label:          'Time'
  x_units:          'S'
  y_label:          'Measured voltage'
  y_units:          'V'
  integration_time: 0.1 # (s)    # This is not implemented
  stabilize_time:   0.001 # (s)
  ao_channel:       2
  ai_channel:       2
  ai_channel1:      1
  ai_channel2:      2
  stop_timeout:       3   # (s) How much time to give scan loop to stop before forcefully terminating it
  gui_refresh_time:   .01     # (s) How often gui checks if here's new data (usually quicker than time_step)

# set limits for the analog out channels and optionally give them custom display names
ao:
  1:
    name:           Channel 1
    upper_limit:    5.4       # (Volt)
    lower_limit:    -5.4      # (Volt)
  2:
    name:           Channel 2
    upper_limit:    5.4       # (Volt)
    lower_limit:    -5.4      # (Volt)

# set parameters for the monitor here
monitor:
  time_step:        0.050   # (s) Note that the basic analog approach doesn't really go faster than 0.010 seconds
  plot_points:      110
  1:
    name:           AI Channel 1
    xlabel:         'time'
  2:
    name:           AI Channel 2
  gui_refresh_time: .01     # (s) How often gui checks if here's new data (usually quicker than time_step)
  text_update_time: .5      # (s) Minimum time for the gui to update the value displayed as text
  stop_timeout:     1       # (s) How much time to give monitor to stop before forcefully terminating it

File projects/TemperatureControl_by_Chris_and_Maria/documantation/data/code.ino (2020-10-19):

// Declare components of the circuit, Pins used, Temperatures

float R= 150; // Resistance used in circuit
float r_0= 100; //Thermistor at 0 Celcius
float a= 0.0039 ;// constant characterizing thermistor 

int PIN_HEATING= 2;
int PIN_COOLING =13;
int PIN_EMERGENCY= 41;
int PIN_MASTER =51;


int T_L =15;
int T_H= 30;
int H_D= 35;
int L_D= 10;

//-------------------------------------------------------------------------------------------------
void setup() {
  Serial.begin(9600);
 }

//Reads Output voltage in arduino units and translate it into degrees. (Voltage divider)

float read_Temperature(){
  float sensor = analogRead(A0);
  float x = (R/r_0)*(1023/sensor -1) -1;
  float T= x/a ;
  return T;    
  }

// Control functions for the response of arduino
void activate_heater(){
  digitalWrite(PIN_COOLING,LOW);
  digitalWrite(PIN_HEATING,HIGH); }

void activate_cooler(){
  digitalWrite(PIN_HEATING,LOW);
  digitalWrite(PIN_COOLING,HIGH);}

void deactivate(){
  digitalWrite(PIN_COOLING,LOW);
  digitalWrite(PIN_HEATING,LOW);}

void danger(){
  deactivate();
  digitalWrite(PIN_EMERGENCY,HIGH);
  delay(360000);
                                //The red button. If T exceeds prespecified temp, it sends a message to master. It shuts down any cooling or heating and sleeps for an hour;
  }



//MAIN----------------------------------------------------------------------------------------------------------------------

void loop() {
 float T = read_Temperature();
 if (T<L_D or T> H_D){danger();}
 
 if (T<T_H){
    activate_cooler();  }
 
 else if (T>T_L){
    activate_heater();}
 
 else{ deactivate();}
 Serial.print("Temperature = ");
 Serial.println(T); 
 Serial.println ("*C");
 delay(20000) ;
}

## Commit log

2020-09-20 merged two SamplePreparation folders
2020-09-28 Upload New File
    [dataypr1.xlsx]
2020-09-28 Update power supply needs subproject_collection.md
2020-09-29 Update projects/Hardware_Johanna_Floris_Frank/Arduino_code/.gitkeep, projects/Hardware_Johanna_Floris_Frank/Arduino_code/BME.ino, projects/Hardware_Johanna_Floris_Frank/Arduino_code/master_reader.io.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
2020-10-05 power rangers
2020-10-05 Added temp sensor
2020-10-05 Updated and added pres sensor
2020-10-05 Update README.md current state and roadmap 05-10-2020
2020-10-05 updates to stop and start arduino
2020-10-07 Update correct power supply order
2020-10-07 Added Finn Pipetting to intructions.md
2020-10-08 Add temperature instructions
2020-10-10 Add arduinodirectory
2020-10-11 Add new directory to store all Arduino controller files
2020-10-11 Upload Arduino Control
2020-10-11 Add readme with explanation of arduino control
2020-10-12 picture arduino
2020-10-12 Improved Readme
    [Data_FFT_Spectra.xlsx]
2020-10-12 Updates and example measurements
    [exampleMeasurementAD2.csv]
2020-10-14 Upload New File: Temperature Control Reproduction Feedback
2020-10-17 Update projects/Stabilization_by_Mark_and_Stijn/Measurements/Acceleration_Measurements/FFT/AccelerationTestNoErrorBars.png, projects/Stabilization_by_Mark_and_Stijn/Measurements/Acceleration_Measurem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
    [Data_FFT_Spectra.xlsx, dataypr1.xlsx]
